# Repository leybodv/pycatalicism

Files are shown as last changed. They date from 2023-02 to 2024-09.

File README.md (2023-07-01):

<h1>pycatalicism</h1>
<p>Программа для контроля оборудования для измерения каталитических характеристик материалов в проточном режиме в реакциях окисления CO и гидрирования CO<sub>2</sub> с образованием CO и алканов до пентана. Оборудование состоит из 3х регуляторов расхода газа, печи и хроматографа. Контроль температуры печи осуществляется с помощью ПИД регулятора. Также с помощью программы можно проводить расчёт основных параметров: конверсии (степени превращения) каталитической реакции, активности и селективности.</p>
  <h2>Содержание</h2>
  <ol>
    <li><a href="#installation">Установка программы</a></li>
    <li><a href="#calc">Рассчёт параметров</a></li>
    <li><a href="#furnace-control">Управление печи</a></li>
    <li><a href="#chromatograph-control">Управление хроматографом</a></li>
    <li><a href="#mfc">Управление регуляторами расхода газов</a></li>
    <li><a href="#valves">Управление соленоидными клапанами</a></li>
    <li><a href="#activation">Проведение активации</a></li>
    <li><a href="#measurement">Проведение измерения</a></li>
    <li><a href="#init-conc-measurement">Проведение измерения исходной концентрации реагентов</a></li>
    <li><a href="#changes">Изменения в новых версиях</a></li>
  </ol>
  <h2 id="installation">Установка программы</h2>
    <h3>Arch Linux</h3>
      <p>Установить python:</p>
      <p><code>pacman -S python</code></p>
      <p>Установить программу:</p>
      <p><code>pip install pycatalicism</code></p>
    <h3>Windows</h3>
      <p>Установить python отсюда: <a href="python.org">python.org</a></p>
      <p>Установить <a href="https://www.microsoft.com/en-us/download/details.aspx?id=48145">Visual C++ Redistributable for Visual Studio 2015</a></p>
      <p>Установить программу:</p>
      <p><code>pip install pycatalicism</code></p>
      <p>Скачать и установить драйвер usb -> com отсюда: <a href="https://www.silabs.com/developers/usb-to-uart-bridge-vcp-drivers">silabs.com</a></p>
  <h2 id="calc">Рассчёт характеристик катализаторов</h2>
    <p><code>pycat calc --conversion|--selectivity [--output-data OUTPUT_DATA] [--show-plot] [--output-plot OUPUT_PLOT] [--products-basis] [--sample-name SAMPLE_NAME] input-data-path initial-data-path {co-oxidation|co2-hydrogenation}</code></p>
    <p>Аргументы:</p>
    <table>
      <tr>
        <td>input-data-path</td>
        <td>путь к папке с файлами, содержащими данные о концентрациях компонентов реакции, температуре и потоках газов</td>
      </tr>
      <tr>
        <td>initial-data-path</td>
        <td>путь к файлу с данными о начальной концентрации компонентов реакции</td>
      </tr>
      <tr>
        <td>{co-oxidation|co2-hydrogenation}</td>
        <td>реакция, для которой провести расчёт</td>
      </tr>
    </table>
    <p>Флаги:</p>
    <table>
      <tr>
        <td>--conversion|--selectivity</td>
        <td>следует ли провести расчёт конверсии и/или селективности (по крайней мере один из вариантов должен быть указан)</td>
      </tr>
      <tr>
        <td>--ouput-data OUPUT_DATA</td>
        <td>путь к папке, в которую сохранить результаты расчёта</td>
      </tr>
      <tr>
        <td>--show-plot</td>
        <td>показать график зависимости конверсии/селективности от температуры</td>
      </tr>
      <tr>
        <td>--ouput-plot OUTPUT_PLOT</td>
        <td>путь к папке, в которую сохранить график зависимости конверсии/селективности</td>
      </tr>
      <tr>
        <td>--products-basis</td>
        <td>рассчитать конверсию из данных о концентрации продуктов, вместо исходных компонентов</td>
      </tr>
      <tr>
        <td>--sample-name</td>
        <td>id образца будет добавлено в файл с результатами расчёта, а также на график</td>
      </tr>
    </table>
    <br>
    <p>Для расчёта конверсии и селективности программе необходимо знать исходные параметры, измеренные на входе в реактор, и параметры на выходе из реактора, полученные в результате измерения при различных температурах реакции. Минимальные параметры для расчёта: концентрации компонентов реакции в мол.% и температуры, при которых проводились измерения. Данные для расчёта должны сохраняться в файлах в определённом формате:</p>
    <div><pre>
    Температура&lt;tab&gt;<i>temperature</i>
    &lt;br&gt;
    Название&lt;tab&gt;Концентрация
    <i>compound-name</i>&lt;tab&gt;<i>compound-concentration</i>
    [&lt;br&gt;
    Темп. (газовые часы)&lt;tab&gt;<i>flow-temperature</i>
    Давление (газовые часы)&lt;tab&gt;<i>flow-pressure</i>
    Поток&lt;tab&gt;<i>flow-rate</i>]
    </pre></div>
    <p>Если файл содержит данные в неверном формате, такой файл игнорируется, а соответствующее сообщение выводится в консоль.</p>
    <table>
      <tr>
        <td><i>temperature</i></td>
        <td>температура, при которой проводилось измерение концентраций и которая будет использоваться в качестве данных оси абсцисс для построения графиков</td>
        <td></td>
      </tr>
      <tr>
        <td><i>compound-name</i></td>
        <td>название компонента реакции</td>
        <td rowspan="2">эта таблица получается копированием данных результатов расчётов из программы Хроматэк Аналитик. Помимо этих данных в таблице также могут присутствовать столбцы других значений (напр. высота пика, площадь и т.п.), что не влияет на конечный результат</td>
      </tr>
      <tr>
        <td><i>compound-concentraion</i></td>
        <td>концентрация компонента в мол.%</td>
      </tr>
      <tr>
        <td><i>flow-temperature</i></td>
        <td>температура в точке измерения общего потока газов в °C</td>
        <td rowspan="3">Данные параметры должны быть измерены с помощью газовых часов на выходе из реактора. Эти параметры не являются необходимыми для расчёта характеристик катализатора. Если они не будут указаны в файле, параметры всё равно будут рассчитаны, однако, в результатах будет ошибка, связанная с изменением объёма реагентов.</td>
      </tr>
      <tr>
        <td><i>flow-pressure</i></td>
        <td>давление в точке измерения общего потока газов в Па</td>
      </tr>
      <tr>
        <td><i>flow-rate</i></td>
        <td>общий поток газов в мл/мин</td>
      </tr>
    </table>
    <p>Рассчёты проводятся с использованием следующих уравнений:</p>
    <p><b>Окисление CO</b></p>
    <pre>https://latex.codecogs.com/svg.image?\alpha = \frac{\frac{p_{i}\cdot f_{i}}{T_{i}}\cdot C_{CO,i} - \frac{p_f\cdot f_f}{T_f}\cdot C_{CO,f}}{\frac{p_{i}\cdot f_{i}}{T_{i}}\cdot C_{CO,i}}</pre>
    <p>
      где<br>
      https://latex.codecogs.com/svg.image?\inline \alpha - конверсия CO<br>
      https://latex.codecogs.com/svg.image?\inline C_{CO,i}, https://latex.codecogs.com/svg.image?\inline C_{CO,f} - концентрации CO до и после каталитического реактора, соответственно, в мол.%<br>
      https://latex.codecogs.com/svg.image?\inline f_{i}, https://latex.codecogs.com/svg.image?\inline f_{f} - общий поток газов до и после каталитического реактора, соответственно, в м<sup>3</sup>/с<br>
      https://latex.codecogs.com/svg.image?\inline p_i, https://latex.codecogs.com/svg.image?\inline p_f - давление в точке измерения общего потока газов до и после каталитического реактора, соответственно, в Па<br>
      https://latex.codecogs.com/svg.image?\inline T_i, https://latex.codecogs.com/svg.image?\inline T_f - температура в точке измерения общего потока газов до и после каталитического реактора, соответственно, в К
    </p>
    <p><b>Гидрирование CO<sub>2</sub></b></p>
    <pre>https://latex.codecogs.com/svg.image?\inline alpha = \frac{\frac{p_{i}\cdot f_{i}}{T_{i}}\cdot C_{CO_2,i} - \frac{p_f\cdot f_f}{T_f}\cdot C_{CO_2,f}}{\frac{p_{i}\cdot f_{i}}{T_{i}}\cdot C_{CO_2,i}}</pre>
    <p>
      где<br>
      https://latex.codecogs.com/svg.image?\inline \alpha - конверсия CO<sub>2</sub><br>
      https://latex.codecogs.com/svg.image?\inline C_{CO_2,i}, https://latex.codecogs.com/svg.image?\inline C_{CO_2,f} - концентрации CO<sub>2</sub> до и после каталитического реактора, соответственно, в мол.%<br>
      https://latex.codecogs.com/svg.image?\inline f_{i}, https://latex.codecogs.com/svg.image?\inline f_{f} - общий поток газов до и после каталитического реактора, соответственно, в м<sup>3</sup>/с<br>
      https://latex.codecogs.com/svg.image?\inline p_i, https://latex.codecogs.com/svg.image?\inline p_f - давление газа в точке измерения общего потока газов до и после каталитического реактора, соответственно, в Па<br>
      https://latex.codecogs.com/svg.image?\inline T_i, https://latex.codecogs.com/svg.image?\inline T_f - температура газа в точке измерения общего потока газов до и после каталитического реактора, соответственно, в К
    </p>
    <pre>https://latex.codecogs.com/svg.image?\inline S = \frac{n_i\cdot C_i}{\sum n_i\cdot C_i}</pre>
    <p>
      где<br>
      S - селективность по отношению компонента i<br>
      https://latex.codecogs.com/svg.image?\inline C_i - концентрация компонента i (CO, CH<sub>4</sub>, C<sub>2</sub>H<sub>6</sub>, C<sub>3</sub>H<sub>8</sub>, i-C<sub>4</sub>H<sub>10</sub>, n-C<sub>4</sub>H<sub>10</sub>, i-C<sub>5</sub>H<sub>12</sub>, n-C<sub>5</sub>H<sub>12</sub>), в мол.%<br>
      n - стехиометрический коэффициент в реакции гидрирования CO<sub>2</sub> (количество атомов C в молекуле продукта)
    </p>
    <p><b>гидрирование CO<sub>2</sub>, расчёт на основе продуктов реакции</b></p>
    <p>Данный метод может быть использован для расчёта конверсии углекислого газа, однако, результат может содержать ошибку, связанную с предположением, что только использованные для расчёта компоненты образовались в результате реакции.</p>
    <pre>https://latex.codecogs.com/svg.image?\inline \alpha = \frac{\sum{n_p\cdot C_p}}{C_{CO_2,i}}\cdot \frac{p_f \cdot f_f \cdot T_i}{p_i \cdot f_i \cdot T_f}</pre>
    <p>
      где<br>
      https://latex.codecogs.com/svg.image?\inline C_{CO_2,i} - концентрация CO<sub>2</sub> до каталитического реактора в мол.%<br>
      https://latex.codecogs.com/svg.image?\inline C_p - концентрации компонента p (CO, CH<sub>4</sub>, C<sub>2</sub>H<sub>6</sub>, C<sub>3</sub>H<sub>8</sub>, i-C<sub>4</sub>H<sub>10</sub>, n-C<sub>4</sub>H<sub>10</sub>, i-C<sub>5</sub>H<sub>12</sub>, n-C<sub>5</sub>H<sub>12</sub>), в мол.%<br>
      n - стехиометрический коэффициент в реакции гидрирования CO<sub>2</sub> (количество атомов C в молекуле продукта)<br>
      https://latex.codecogs.com/svg.image?\inline f_{i}, https://latex.codecogs.com/svg.image?\inline f_{f} - общий поток газов до и после каталитического реактора, соответственно, в м<sup>3</sup>/с<br>
      https://latex.codecogs.com/svg.image?\inline p_i, https://latex.codecogs.com/svg.image?\inline p_f - давление газа в точке измерения общего потока газа до и после каталитического реактора, соответственно, в Па<br>
      https://latex.codecogs.com/svg.image?\inline T_i, https://latex.codecogs.com/svg.image?\inline T_f - температура газа в точке измерения общего потока газа до и после каталитического реактора, соответственно, в К
    </p>
    <p>В случае, если данные об измерении общего потока газа не были измерены, конверсия рассчитывается только на основе данных о концентрациях, а в консоль выводится предупреждение.</p>
  <h2 id="furnace-control">Контроль печи</h2>
  <p>Контроль печи осуществляется с помощью контроллера ОВЕН ТРМ101, связь с которым устанавливается через последовательный порт. Параметры конфигурации контроллера должны быть прописаны в файле <a href="https://github.com/leybodv/pycatalicism/blob/main/pycatalicism/config.py">config.py</a></p>
    <p><code>pycat furnace set-temperature temperature</code></p>
    <p>Устанавить значение параметра SP регулятора.</p>
    <p>Аргументы:</p>
    <p>
      <table>
        <tr>
          <td>temperature</td>
          <td>Температура в °C</td>
        </tr>
      </table>
    </p>
    <p><code>pycat furnace print-temperature</code></p>
    <p>Вывести измеренную температуру в консоль.</p>
  <h2 id="chromatograph-control">Управление хроматографом</h2>
    <p>Осуществляется управление хроматографом Хроматэк Кристалл 5000 через протокол Modbus. Для работы протокола необходимо, чтобы был запущен сервер Modbus, в качестве которого выступают Панель управления и Аналитик, а также специальная программа, которую необходимо установить с установочного диска ПО Хроматэк (см. документацию Modbus из комплекта документации Хроматэк для более детальной инструкции). Перед работой с pycatalytic, необходимо добавить нужные регистры Modbus в Панели управления и Аналитик. Список необходимых регистров прописывается в конфигурации программы и может быть найден здесь: <a href="https://github.com/leybodv/pycatalicism/blob/main/pycatalicism/config.py">config.py</a></p>
    <p><b>Доступные комманды:</b></p>
    <p><code>pycat chromatograph set-method method</code></p>
    <p>Устанавливает инструментальный метод хроматографа. Хроматограф переходит в режим "Подготовка". Список методов должен быть в <a href="https://github.com/leybodv/pycatalicism/blob/main/pycatalicism/config.py">config.py</a>. Если Панель управления и Аналитик не запущены, запускает их, устанавливает соединение с хроматографом. В этом случае программа ждёт успешного запуска Панели управления и Аналитика, а также установления соединения. Если, при этом, хроматограф выключен, программа зависнет.</p>
    <p>Аргументы:</p>
    <p>
      <table>
        <tr>
          <td>method</td>
          <td>инструментальный метод хроматографа</td>
        </tr>
      </table>
    </p>
    <p><code>pycat chromatograph start-analysis</code></p>
    <p>Начинает измерение.</p>
    <p><code>pycat chromatograph set-passport --name NAME [--volume VOL] [--dilution DIL] [--purpose {analysis|graduation}] --operator OP --column COL [--lab-name LN]</code></p>
    <p>Устанавливает значения паспорта хроматограммы. Эта команда должна использоваться только после окончания анализа на хроматографе.</p>
    <p>Необходимые параметры:</p>
    <p>
      <table>
        <tr>
          <td>--name NAME</td>
          <td>название хроматограммы</td>
        </tr>
        <tr>
          <td>--operator OP</td>
          <td>оператор</td>
        </tr>
        <tr>
          <td>--column COL</td>
          <td>название колонки</td>
        </tr>
      </table>
    </p>
    <p>Опциональные параметры:</p>
    <p>
      <table>
        <tr>
          <td>--volume VOL</td>
          <td>объём пробы, 0.5 по умолчанию</td>
        </tr>
        <tr>
          <td>--dilution DIL</td>
          <td>разбавление пробы, 1 по умолчанию</td>
        </tr>
        <tr>
          <td>--purpose {analysis|graduation}</td>
          <td>назначение хроматограммы, analysis по умолчанию</td>
        </tr>
        <tr>
          <td>--lab-name LN</td>
          <td>название лаборатории, Inorganic Nanomaterials по умолчанию</td>
        </tr>
      </table>
    </p>
  <h2 id="mfc">Управление регуляторами расхода газов</h2>
  <p>Программа осуществляет управление регуляторами расхода газов Bronkhorst F201CV для регулирования потока He, CO<sub>2</sub>, O<sub>2</sub>, H<sub>2</sub>, CO или CH<sub>4</sub>. Параметры соответствующих регуляторов расхода газов должны быть прописаны в файле <a href="https://github.com/leybodv/pycatalicism/blob/main/pycatalicism/config.py">config.py</a></p>
  <p><code>pycat mfc set-flow-rate --gas {He|CO2|O2|H2|CO|CH4} --flow-rate FR</code></p>
  <p>Устанавливает поток газа</p>
  <p>
    <table>
      <tr>
        <td>--gas {He|CO2|O2|H2|CO|CH4}</td>
        <td>газ, для которого необходимо установить поток. Программа выбирает регулятор на основе этого значения</td>
      </tr>
      <tr>
        <td>--flow-rate FR</td>
        <td>поток газа в н.мл/мин</td>
      </tr>
    </table>
  </p>
  <p><code>pycat mfc set-calibration --gas {He|CO2|O2|H2|CO|CH4} --calibration-number CN</code></p>
  <p>Устанавливает калибровку регулятора расхода газа</p>
  <p>
    <table>
      <tr>
        <td>--gas {He|CO2|O2|H2|CO|CH4}</td>
        <td>газ, для которого необходимо установить калибровку. Программа выбирает регулятор на основе этого значения</td>
      </tr>
      <tr>
        <td>--calibration-number CN</td>
        <td>номер калибровки, указанный в документации, поставляемой с прибором</td>
      </tr>
    </table>
  </p>
  <p><code>pycat mfc print-flow-rate --gas {He|CO2|O2|H2|CO|CH4}</code></p>
  <p>Выводит измеренный поток газа в консоль в н.мл/мин</p>
  <p>
    <table>
      <tr>
        <td>--gas {He|CO2|O2|H2|CO|CH4}</td>
        <td>газ, для которого нужно показать поток. Программа выбирает регулятор на основе этого значения</td>
      </tr>
    </table>
  </p>
  <h2 id="valves">Управление соленоидными клапанами</h2>
  <p>Программа осуществляет управление соленоидными клапанами VSAA, подключёнными к ардуино согласно схеме <a href="https://github.com/leybodv/pycatalicism/blob/main/wiring/valve-controller_scheme.png">scheme</a>. Соответствие номеров клапанов и соответствующих им газов должно быть прописано в файле <a href="https://github.com/leybodv/pycatalicism/blob/main/pycatalicism/config.py">config.py</a>.</p>
  <p><code>pycat valve set-state --gas G --state {open|close}</code></p>
  <p>Изменяет состояние клапана</p>
  <p>
    <table>
      <tr>
        <td>--gas G</td>
        <td>газ, для которого необходимо изменить состояние клапана. Должен быть прописан в файле конфигурации</td>
      </tr>
      <tr>
        <td>--state {open|close}</td>
        <td>open - открыть клапан<br>close - закрыть клапан</td>
      </tr>
    </table>
  </p>
  <p><code>pycat valve get-state --gas G</code></p>
  <p>Запрашивает состояние клапана</p>
  <p>
    <table>
      <tr>
        <td>--gas G</td>
        <td>газ, для которого запрашивается состояние клапана. Должен быть прописан в файле конфигурации</td>
      </tr>
    </table>
  </p>
  <h2 id="activation">Активация</h2>
  <p>Проведение активации катализатора перед анализом свойств. Для проведения активации все газы должны быть подключены к системе, клапаны открыты. Режим активации задаётся в файле конфигурации, пример которого можно посмотреть здесь: <a href="https://github.com/leybodv/pycatalicism/blob/main/pycatalicism/activation_config.py">activation_config.py</a>. После запуска программа устанавливает заданные в конфигурации потоки, продувает систему в течение 30 мин, греет печь до указанной температуры, проводит выдержку при данной температуре в течение указанного в конфигурации времени и отключают нагрев. После охлаждения ниже определённой температуры потоки газов меняются на новые, указанные в конфигурации. При активации строятся графики зависимости температуры и потоков газов от времени. После окончания активации, для того, чтобы остановить построение графика, нужно нажать Enter в командной строке.</p>
  <p><code>pycat activate --config CONFIG</code></p>
  <p>
    <table>
      <tr>
        <td>--config CONFIG</td>
        <td>путь к файлу конфигурации с параметрами активации</td>
      </tr>
    </table>
  </p>
  <h2 id="measurement">Проведение измерения</h2>
  <p>Проведение измерения состава газа после реактора при различных температурах. Программа проводит продувку хроматографа перед анализом (запускает метод purge на хроматографе), проводит нагрев до температуры измерения, ждёт заданное время, запускает измерение хроматограммы и повторяет данную процедуру для каждой температуры анализа. После окончания анализа программа выключает печь и запускает охлаждение хроматографа. Все параметры измерения должны быть указаны в файле конфигурации, пример которого можно найти здесь: <a href="https://github.com/leybodv/pycatalicism/blob/main/pycatalicism/measurement_config.py">measurement_config.py</a>. При измерении строятся графики зависимости температуры, потоков газов от времени, а также отмечаются моменты времени начала анализа хроматографом.</p>
  <p><code>pycat measure --config CONFIG</code></p>
  <p>
    <table>
      <tr>
        <td>--config CONFIG</td>
        <td>путь к файлу конфигурации с параметрами измерения</td>
      </tr>
    </table>
  </p>
  <h2 id="init-conc-measurement">Проведение измерения исходной концентрации реагентов</h2>
  <p>Проведение серии измерений состава газа при комнатной температуре. Результаты измерений необходимы для расчёта конверсии реакции. Программа устанавливает потоки газов, запускает продувку хроматографа (метод purge) и снимает несколько хроматограмм. По завершении запускает охлаждение хроматографа (метод cooling). Параметры проведения эксперимента должны быть указаны в файле конфигурации, пример которого можно найти здесь: <a href="https://github.com/leybodv/pycatalicism/blob/main/pycatalicism/init_conc_config.py">init_conc_config.py</a>. При измерении строятся графики зависимости температуры, потоков газов от времени, а также отмечаются моменты времени начала анализа хроматографом.</p>
  <p><code>pycat measure-init-concentration --config CONFIG</code></p>
  <p>
    <table>
      <tr>
        <td>--config CONFIG</td>
        <td>путь к файлу конфигурации с параметрами измерения</td>
      </tr>
    </table>
  </p>
  <h2>ТуДу</h2>
    <ul>
      <li>переписать модуль calc: селективность должна рассчитываться автоматически, если это имеет смысл; должно быть 2 команды <code>calculate activity</code> и <code>calculate conversion</code></li>
      <li>автоматически конвертировать данные с газовых часов в СИ при рассчёте</li>
    </ul>
  <h2 id="changes">Изменения в новых версиях</h2>
    <ul>
      <li>2.0.1</li>
      <p>Исправлена ошибка <a href="https://github.com/leybodv/pycatalicism/issues/19">issue 19</a></p>
      <li>2.0.2</li>
      <p>Исправлена ошибка <a href="https://github.com/leybodv/pycatalicism/issues/1">issue 1</a></p>
    </ul>

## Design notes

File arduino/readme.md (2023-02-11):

<h1>Протокол связи между pycat и pycatuino</h1>
<h2>v.0</h2>
<p>Обмен сообщениями происходит в ASCII формате. Ведущее устройство отправляет сообщение в формате "ведущий -> ведомый". На каждое сообщение ведомое устройство отправляет ответ в формате "ведомый -> ведущий".</p>
<p>Формат сообщения (ведущий -> ведомый):</p>
<table>
  <tr>
    <td>@</td>
    <td>&lt;command&gt;</td>
    <td>.</td>
    <td>&lt;devnum&gt;</td>
    <td>.</td>
    <td>&lt;value&gt;</td>
    <td>#</td>
  </tr>
</table>
<table>
  <tr>
    <td>&lt;command&gt;</td>
    <td>SET - установить значение клапана &lt;devnum&gt;<br>GET - запросить состояние клапана &lt;devnum&gt; (значение &lt;value&gt; должно быть NONE)<br>HSH - приветствие (значение devnum может быть любым от 1 до 5)</td>
  </tr>
  <tr>
    <td>&lt;devnum&gt;</td>
    <td>Номер клапана от 1 до 5</td>
  </tr>
  <tr>
    <td>&lt;value&gt;</td>
    <td>OPEN - открыть клапан<br>CLOSE - закрыть клапан<br>NONE - значение при запросе состояния клапана<br>NISMF - слово приветствие</td>
  </tr>
</table>
<p>Формат ответа (ведомый -> ведущий)</p>
<table>
  <tr>
    <td>@</td>
    <td>&lt;devstat&gt;</td>
    <td>.</td>
    <td>&lt;value&gt;</td>
    <td>#</td>
  </tr>
</table>
<table>
  <tr>
      <td>&lt;devstat&gt;</td>
      <td>OK - последняя операция выполнена успешно<br>ERR - последняя операция выполнена с ошибками<br>HSH - ответ на приветствие<br>ANS - ответ на команду GET</td>
  </tr>
  <tr>
    <td>&lt;value&gt;</td>
    <td>OPEN|CLOSE - открыт или закрыт клапан (высылается при успешном выполнении последней операции или при ответе на запрос ведущего устройства)<br>&lt;errcode&gt; - код ошибки<br>DBQWT - слово ответа на приветствие</td>
  </tr>
</table>
<p>Коды ошибок</p>
<table>
  <tr>
    <td>MSGFMT</td>
    <td>Неверный формат сообщения</td>
  </tr>
  <tr>
    <td>DVNM</td>
    <td>Ошибка в номере клапана &lt;devnum&gt;</td>
  </tr>
  <tr>
    <td>HNDSHK</td>
    <td>Ошибка в слове приветствия</td>
  </tr>
  <tr>
    <td>VL</td>
    <td>Ошибка в значении &lt;value&gt;</td>
  </tr>
</table>

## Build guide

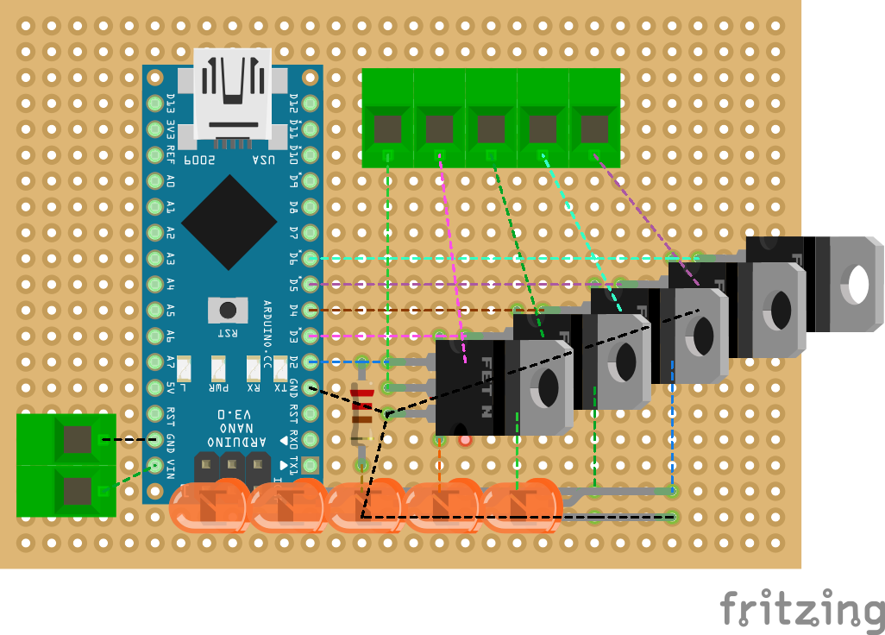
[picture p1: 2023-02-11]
wiring/valve-controller_bb.png

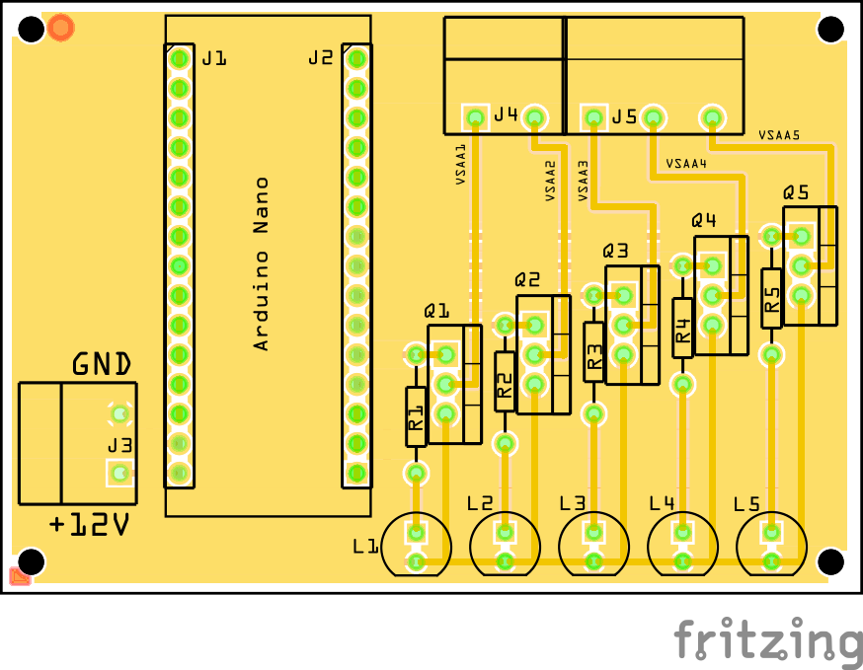
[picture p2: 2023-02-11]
wiring/valve-controller_pcb-top.png

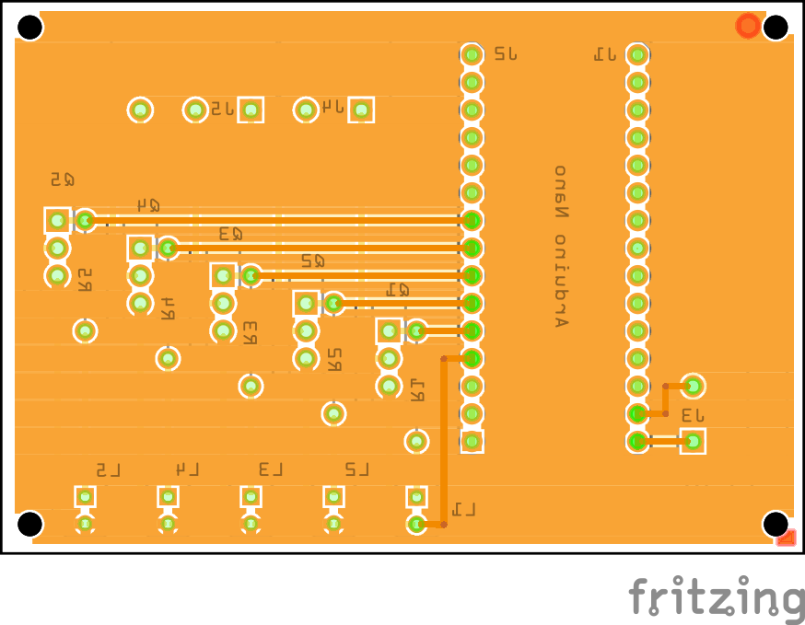
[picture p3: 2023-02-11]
wiring/valve-controller_pcb-bottom.png

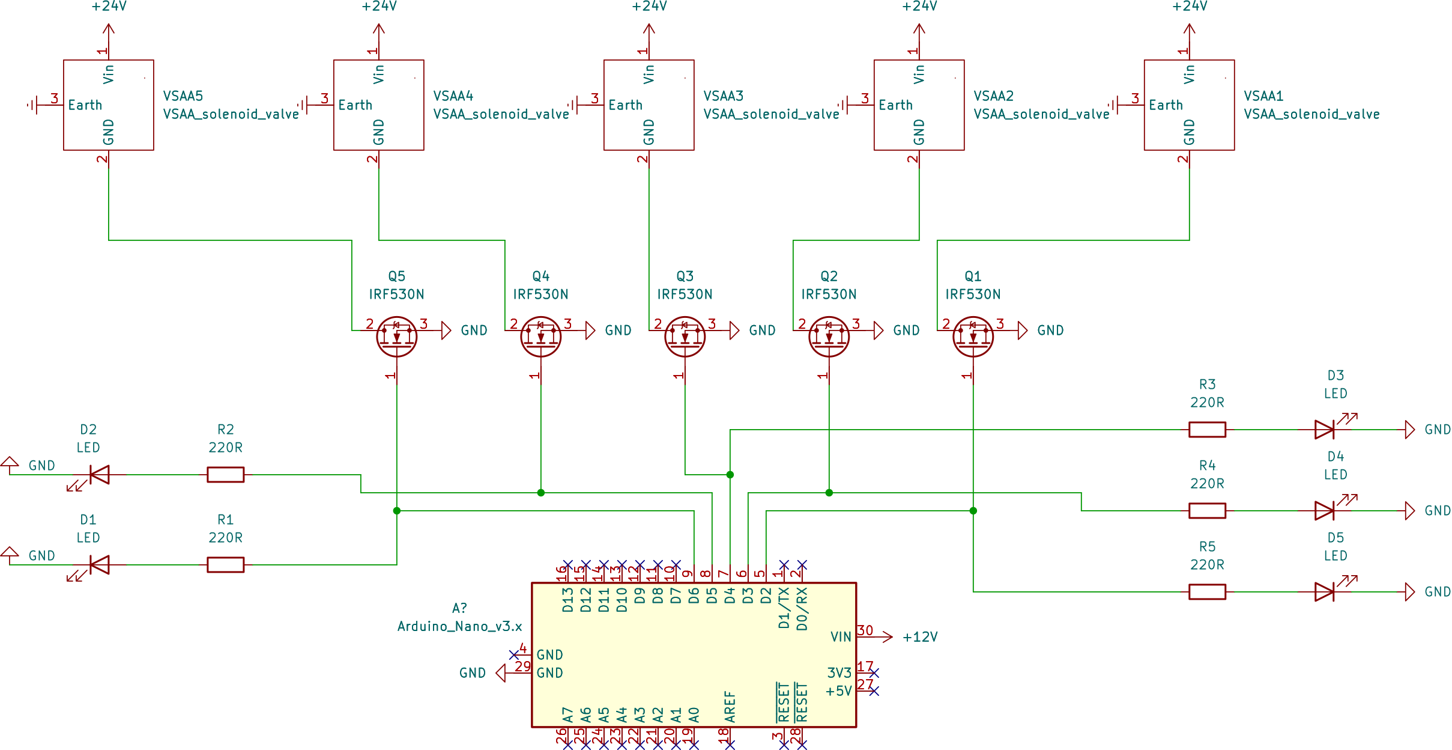
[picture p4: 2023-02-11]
wiring/valve-controller_scheme.png

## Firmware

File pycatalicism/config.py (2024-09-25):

import serial

# parser type used to convert raw data from equipment for gas composition measurement to input data for calculator to calculate conversion/activity/selectivity vs. temperature
#
# chromatec-crystal-composition-copy-paste
#   raw data obtained via copy/paste of composition calculation results from chromatec analytics software
#   data must be in a format:
#   Температура<tab><temperature>
#   <br>
#   Название<tab>Время, мин<tab>Детектор<tab>Концентрация<tab>Ед, измерения<tab>Площадь<tab>Высота
#   <compound-name><tab><retention-time><tab><detector-name><tab><compound-concentration><tab><concentration-units><tab><peak-area><tab><peak-height>
#   [<br>
#   Темп. (газовые часы)<tab><flow-temperature>
#   Давление (газовые часы)<tab><flow-pressure>
#   Поток<tab><flow-rate>]
raw_data_parser_type = 'chromatec-crystal-composition-copy-paste'

# logging levels for different classes/modules
import logging
from datetime import datetime
logging_levels = {
                    'ChromatecCrystalCompositionCopyPasteParser'    :   logging.INFO,
                    'CO2HydrogenationCalculator'                    :   logging.INFO,
                    'CO2HydrogenationProductsBasisCalculator'       :   logging.INFO,
                    'CO2HydrogenationExporter'                      :   logging.INFO,
                    'CO2HydrogenationPlotter'                       :   logging.INFO,
                    'COOxidationCalculator'                         :   logging.INFO,
                    'COOxidationExporter'                           :   logging.INFO,
                    'COOxidationPlotter'                            :   logging.INFO,
                    'RawData'                                       :   logging.INFO,
                    }
# path to file to which logs will be written
logfilepath=f'./pycatalicism_logs/{datetime.now():%Y%m%d_%H%M%S}.log'

## chromatograph configuration ##
# slave id in control panel modbus configuration
control_panel_modbus_id = 1
# register with working status of chromatograph
working_status_input_address = 0
# register with step time in minutes
step_time_input_address = 18
# register with connection status
connection_status_input_address = 17
# register with current instrumental method
method_holding_address = 0
# register with chromatograph command
chromatograph_command_holding_address = 2
# register with control panel application command
application_command_holding_address = 3
# slave id in analytic modbus configuration
analytic_modbus_id = 2
# register with chromatogram nams
sample_name_holding_address = 0
# register with chromatogram purpose
chromatogram_purpose_holding_address = 15
# register with sample's volume
sample_volume_holding_address = 17
# register with sample's dilution
sample_dilution_holding_address = 21
# register with operator's name
operator_holding_address = 25
# register with column name
column_holding_address = 40
# register with lab name
lab_name_holding_address = 55
# list of methods with their order number at control panel software
methods = {
        '20220415_O2-N2-CO2-CO-C1,5HxAlkanes_2levels'	:		0,
        'co2-hydrogenation'								:		1,
        'cooling'										:		2,
        'co-oxidation'									:		3,
        'crm'											:		4,
        'Marusya method'								:		5,
        'NaX-conditioning'								:		6,
        'NaX-HaesepN-conditioning'						:		7,
        'purge'											:		8,
        'purge-overnight'								:		9,
        'zero'											:		10,
        'Водка-Маруся'									:		11,
        }

## mass flow controllers configuration ##
from pycatalicism.mass_flow_controller.bronkhorst_mfc_calibration import BronkhorstMFCCalibration
mfc_He_serial_address = 'COM3'
mfc_He_serial_id = 'M21212791C'
# NB: calibration ordering starts from 0 here, so, calibration for fluid1 has 0th number
mfc_He_calibrations = {
                    0	:	BronkhorstMFCCalibration(max_flow_rate=100, gas='He', p_in=3, p_out=1),
                    1	:	BronkhorstMFCCalibration(max_flow_rate=100, gas='He', p_in=32, p_out=30),
                    }
mfc_CO2_serial_address = 'COM4'
mfc_CO2_serial_id = 'M21212791E'
mfc_CO2_calibrations = {
                    0	:	BronkhorstMFCCalibration(max_flow_rate=100, gas='CO2', p_in=3, p_out=1),
                    1	:	BronkhorstMFCCalibration(max_flow_rate=100, gas='CO2', p_in=32, p_out=30),
                    2	:	BronkhorstMFCCalibration(max_flow_rate=100, gas='O2', p_in=3, p_out=1),
                    }
mfc_H2_serial_address = 'COM5'
mfc_H2_serial_id = 'M21212791D'
mfc_H2_calibrations = {
                    0	:	BronkhorstMFCCalibration(max_flow_rate=30, gas='CH4', p_in=3, p_out=1),
                    1	:	BronkhorstMFCCalibration(max_flow_rate=90, gas='CH4', p_in=32, p_out=30),
                    2	:	BronkhorstMFCCalibration(max_flow_rate=100, gas='H2', p_in=3, p_out=1),
                    3	:	BronkhorstMFCCalibration(max_flow_rate=100, gas='H2', p_in=32, p_out=30),
                    4	:	BronkhorstMFCCalibration(max_flow_rate=100, gas='CO', p_in=11, p_out=1),
                    }

## solenoid valves configuration ##
valves_port = 'COM7'
valves_baudrate = 9600
valves_bytesize = serial.EIGHTBITS
valves_parity = serial.PARITY_NONE
valves_stopbits = serial.STOPBITS_ONE
valves_gases = {
                'He'     :  1,
                'CO2'    :  2,
                'O2'     :  2,
                'H2_NH3' :  3,
                'H2'     :  4,
                'CO'     :  4,
                'NH3'    :  5,
                }

## furnace configuration ##
# Furnace controller type
furnace_device_name = 'ÒÐÌ101' # <- this string is actually returned by the device \_O_/ although should be 'TPM101' according to owen protocol
# Furnace controller port name and corresponding port parameters (baudrate, bytesize, parity, stopbits) which must be the same as configured on controller device
furnace_port = 'COM6'
furnace_baudrate = 19200
furnace_bytesize = serial.EIGHTBITS
furnace_parity = serial.PARITY_NONE
furnace_stopbits = serial.STOPBITS_ONE
# Time in seconds to wait for the response from the device
furnace_timeout = 0.1
# Time in seconds to wait while message is sent to the device
furnace_write_timeout = None
# Enable/disable hardware flow control
furnace_rtscts = False
# Address of Owen TRM101 device
furnace_address = 0

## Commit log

2022-04-01 calculate_conversion: use pressure, temperature and flow rate from gas clocks for conversion calculation
2022-04-21 replaced plot-title with sample-name parameter for argparse
2022-04-21 __init__, __str__: added sample name parameter
2022-04-21 calculate: changed plot_title to sample_name parameter
2022-04-21 calculate: passed sample_name as plot_title parameter to plot method
2022-05-05 added sample_name parameter
2022-05-05 calculate_selectivity: added sample name parameter
2022-05-05 get_sorted: added sample_name parameter
2022-05-05 calculate_conversion: added sample_name parameter
2022-05-23 furnace -> heat
2022-05-23 heat: added implementation
2022-05-23 heat: added function
2022-05-23 heat: started to add implementation
2022-05-30 heat: added parameter to export_data method
2022-06-08 heat: changed method logic
2022-06-13 heat: removed unnecessary parameters
2022-07-05 heat: added logging
2022-07-05 added heat command description
2022-08-11 CurrentStep: added enum class
2022-08-16 heat furnace to first temperature
2022-08-18 set_flow_rate: check if flow_rate is bigger than maximum calibration value
2022-08-19 added mass flow controllers config
2022-08-19 get_flow_rate: check if flow_rate_propar is not None
2022-08-20 added mass flow controller usage description
2022-08-28 initialize devices only when they are needed
2022-09-02 measure: wait 10 min, after gas flow rates were set
2022-09-02 measure: include temperature with 1 point precision in sample name
2022-09-02 measure: write chromatogram_temperature as part of name, not current_temperature
2022-09-03 measure: use _initialize_<device> functions
2022-09-03 DataCollectorPlotter: made subclass of threading.Thread
2022-09-09 activate: added actual flow rate checking
2022-09-09 measure: check actual flow rates
2022-09-09 Revert "measure: check actual flow rates"
    This reverts commit 8bcd7f70a2363528a60754f61a9f762c7f3fc71c.
    going to change how this works
2022-09-10 measure_init_conc: check actual flow rates before analysis
2022-09-15 new file: arduino/readme.txt
2022-09-23 read and write registers using threading lock
2022-09-25 modified: arduino/readme.txt
2022-10-01 new file: arduino/stepper_example/stepper_example.ino
2022-12-14 deleted arduino files
2022-12-14 new file: arduino/nano-datasheet.jpg
2022-12-17 adding valve controlling circuit
    [valve-controller.kicad_pcb, valve-controller.kicad_sch]
2022-12-17 making wiring diagram for valve controller
    [valve-controller.kicad_sch]
2022-12-17 fritzing wiring diagram
    [valve-controller.fzz]
2022-12-18 optimizing components location
    [valve-controller.fzz]
2022-12-18 placed components for valve controller
    [valve-controller.fzz]
2022-12-18 drawing valve controller wiring
    [valve-controller.fzz]
2022-12-19 renamed: arduino/protocol.html -> arduino/protocol.md
2022-12-19 renamed: arduino/protocol.md -> arduino/protocol.txt
2022-12-19 renamed: arduino/protocol.txt -> arduino/readme.html
2022-12-19 renamed: arduino/readme.html -> arduino/readme.md
2022-12-21 change valves and transistors order
    [valve-controller.kicad_sch]
2022-12-21 changed valves and transistors order
2022-12-21 sketch for arduino controlling valves
2022-12-23 finished sketch for valves controller
2022-12-23 added description for valve controls
2022-12-23 added configuration for valves
2022-12-23 added valves parser
2022-12-23 valves_set_state: added method
2022-12-23 valves_get_state: added method
2022-12-23 ValveState: added class
2022-12-25 new file: pycatalicism/valves/valves_exceptions.py
2022-12-27 setup: blink with builtin led
2022-12-27 valves_set/get_state: close serial connection
2022-12-27 removed valve_controllse.close
2022-12-30 activate: added multistep activation with valves support
2022-12-30 _set_and_wait_until_temperature_reached: turn off heating if required temperature is 0. Wait until current temperature is inside 1 percent window of the target.
2022-12-30 added support for valves
2022-12-30 measure: added support for valves
2023-01-12 measure_init_conc: added valves support
2023-01-12 added valves support
2023-06-25 send_PIC: round new temperature value to integer it is not multiple of 0.5 (issue #19)
